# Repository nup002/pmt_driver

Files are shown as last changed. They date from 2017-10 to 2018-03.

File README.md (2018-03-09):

# PMT driver
-------------

The PMT driver is a complete system for operating and pulse height triggering on up to four photomultiplier tubes. 
It will output high-precision (92ps jitter typ.) trigger pulses from each channel as LVDS signals on cat5 ethernet cable.
Low-precision trigger pulses are combined with programmable logic so that channels can be set up in coincidence, veto, or any other 
configuration as required for the specific experimental setup.

Specifications and capabilities:
- Input voltage: 18V-36V, recommended 24V.
- Current consumption: 250mA
- Screw terminals for powering and controlling gain of four PMTs (designed for Hamamatsu H10425 series)
- Four LEMO input channels. Per channel:
  - 5.95mV/1µA amplifier (75.5dB). Operational range: 1MHz - 300MHz.
  - Pulse height discriminator (200ps jitter typ.) with adjustable discriminator level and pulse length output.
  - Discriminated pulse output as LVDS over RJ45 connector for standard cat5 ethernet cables. Pulses from each of the four channels are time-matched to +-5ps.
- TTL-level version of the discriminated pulses pass through optional delay lines.
- Discriminated pulses are combined with programmable logic, so that nearly any required experimental configuration can be implemented. 
- Final pulse is output over LVDS and TTL, with adjustable length.

## Programmable logic
There are four input channels on the PMT driver, designated CH0 to Ch3. CH0 and CH1 are designed as Pair A. CH2 and CH3 are designated as Pair B. 
The TTL pulses that are generated by each discriminator are combined in a block of programmable logic, where the configuration is set by DIP-switches. There are 
three blocks of DIP-switches. The signals of Pair A are combined in block 1. The signals of Pair B are combined in block 2. 
These two signals are then combined to one in block 3. This is the final output. 

The DIP switches works as lookup tables, and their configuration determine what the output of the block will be based on the logic state of the two input channels. 
Each block can therefore be set up to be any logic gate, such as AND, OR, NOR, XOR, NAND, etc, and also other non-standard logic gates.

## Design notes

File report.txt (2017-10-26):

Info: Reading netlist file "C:\Users\pixel\Documents\Kicad projects\pmt_driver\Netlist.net".

Info: Using references to match components and footprints.

Error: No footprint defined for component 'J2'.

Error: No footprint defined for component 'D1'.

Error: No footprint defined for component 'R25'.

Error: No footprint defined for component 'J6'.

Error: No footprint defined for component 'U9'.

Error: No footprint defined for component 'C62'.

Error: No footprint defined for component 'R27'.

Info: Checking netlist component footprint "C1:/59A05019/59E02E3B:Capacitors_THT:CP_Radial_D10.0mm_P5.00mm".

Adding new component "C1:/59A05019/59E02E3B" footprint "Capacitors_THT:CP_Radial_D10.0mm_P5.00mm".

Info: Checking netlist component footprint "C2:/59A05019/59DFEB5B:Capacitors_THT:CP_Radial_D10.0mm_P5.00mm".

Adding new component "C2:/59A05019/59DFEB5B" footprint "Capacitors_THT:CP_Radial_D10.0mm_P5.00mm".

Info: Checking netlist component footprint "C3:/59A05019/59E0031B:Capacitors_SMD:C_1206_HandSoldering".

Adding new component "C3:/59A05019/59E0031B" footprint "Capacitors_SMD:C_1206_HandSoldering".

Info: Checking netlist component footprint "C4:/59A05019/59E03022:Capacitors_THT:CP_Radial_D8.0mm_P3.50mm".

Adding new component "C4:/59A05019/59E03022" footprint "Capacitors_THT:CP_Radial_D8.0mm_P3.50mm".

Info: Checking netlist component footprint "C5:/59A05019/59DFE2C9:Capacitors_SMD:C_1206_HandSoldering".

Adding new component "C5:/59A05019/59DFE2C9" footprint "Capacitors_SMD:C_1206_HandSoldering".

Info: Checking netlist component footprint "C6:/59A05019/59E04BC9:Capacitors_THT:CP_Radial_D8.0mm_P5.00mm".

Adding new component "C6:/59A05019/59E04BC9" footprint "Capacitors_THT:CP_Radial_D8.0mm_P5.00mm".

Info: Checking netlist component footprint "C7:/59A05019/59E06937:Capacitors_THT:CP_Radial_D8.0mm_P5.00mm".

Adding new component "C7:/59A05019/59E06937" footprint "Capacitors_THT:CP_Radial_D8.0mm_P5.00mm".

Info: Checking netlist component footprint "C8:/59A05019/59E05166:Capacitors_THT:CP_Radial_D8.0mm_P5.00mm".

Adding new component "C8:/59A05019/59E05166" footprint "Capacitors_THT:CP_Radial_D8.0mm_P5.00mm".

Info: Checking netlist component footprint "C9:/59A05019/59E06947:Capacitors_THT:CP_Radial_D8.0mm_P5.00mm".

Adding new component "C9:/59A05019/59E06947" footprint "Capacitors_THT:CP_Radial_D8.0mm_P5.00mm".

Info: Checking netlist component footprint "C10:/59A05019/59E04F1C:Capacitors_SMD:C_1206_HandSoldering".

Adding new component "C10:/59A05019/59E04F1C" footprint "Capacitors_SMD:C_1206_HandSoldering".

Info: Checking netlist component footprint "C11:/59A05019/59E0693F:Capacitors_SMD:C_1206_HandSoldering".

Adding new component "C11:/59A05019/59E0693F" footprint "Capacitors_SMD:C_1206_HandSoldering".

Info: Checking netlist component footprint "C12:/59A05019/59E051E6:Capacitors_SMD:C_1206_HandSoldering".

Adding new component "C12:/59A05019/59E051E6" footprint "Capacitors_SMD:C_1206_HandSoldering".

Info: Checking netlist component footprint "C13:/59A05019/59E0694F:Capacitors_SMD:C_1206_HandSoldering".

Adding new component "C13:/59A05019/59E0694F" footprint "Capacitors_SMD:C_1206_HandSoldering".

Info: Checking netlist component footprint "C14:/59A05019/59DFDE0B:Resistors_SMD:R_1206_HandSoldering".

Adding new component "C14:/59A05019/59DFDE0B" footprint "Resistors_SMD:R_1206_HandSoldering".

Info: Checking netlist component footprint "C15:/59A05019/59A07473:Capacitors_SMD:C_0805_HandSoldering".

Adding new component "C15:/59A05019/59A07473" footprint "Capacitors_SMD:C_0805_HandSoldering".

Info: Checking netlist component footprint "C16:/59A05019/59E06927:Capacitors_SMD:C_0805_HandSoldering".

Adding new component "C16:/59A05019/59E06927" footprint "Capacitors_SMD:C_0805_HandSoldering".

Info: Checking netlist component footprint "C17:/59A05019/59E0525E:Capacitors_SMD:C_0805_HandSoldering".

Adding new component "C17:/59A05019/59E0525E" footprint "Capacitors_SMD:C_0805_HandSoldering".

Info: Checking netlist component footprint "C18:/59A05019/59E06957:Capacitors_SMD:C_0805_HandSoldering".

Adding new component "C18:/59A05019/59E06957" footprint "Capacitors_SMD:C_0805_HandSoldering".

Info: Checking netlist component footprint "C19:/59A05019/59E01262:Capacitors_THT:C_Radial_D5_L11_P2".

Adding new component "C19:/59A05019/59E01262" footprint "Capacitors_THT:C_Radial_D5_L11_P2".

Info: Checking netlist component footprint "C20:/59A05019/59E01A68:Capacitors_THT:CP_Radial_D8.0mm_P3.50mm".

Adding new component "C20:/59A05019/59E01A68" footprint "Capacitors_THT:CP_Radial_D8.0mm_P3.50mm".

Info: Checking netlist component footprint "C21:/59A0A1E6/59DC8F61:Capacitors_SMD:C_0805_HandSoldering".

Adding new component "C21:/59A0A1E6/59DC8F61" footprint "Capacitors_SMD:C_0805_HandSoldering".

Info: Checking netlist component footprint "C22:/59A0A1E6/59DD6348:Capacitors_SMD:C_0805_HandSoldering".

Adding new component "C22:/59A0A1E6/59DD6348" footprint "Capacitors_SMD:C_0805_HandSoldering".

Info: Checking netlist component footprint "C23:/59A0A1E6/59DBDC4C:Capacitors_SMD:C_0402".

Adding new component "C23:/59A0A1E6/59DBDC4C" footprint "Capacitors_SMD:C_0402".

Info: Checking netlist component footprint "C24:/59A0A1E6/59DBE8B8:Capacitors_SMD:C_0402".

Adding new component "C24:/59A0A1E6/59DBE8B8" footprint "Capacitors_SMD:C_0402".

Info: Checking netlist component footprint "C25:/59A0A1E6/59D8314A:Capacitors_SMD:C_0306".

Adding new component "C25:/59A0A1E6/59D8314A" footprint "Capacitors_SMD:C_0306".

Info: Checking netlist component footprint "C26:/59A0A1E6/59DBE89D:Capacitors_SMD:C_0306".

Adding new component "C26:/59A0A1E6/59DBE89D" footprint "Capacitors_SMD:C_0306".

Info: Checking netlist component footprint "C27:/59A0A1E6/59D8318E:Capacitors_SMD:C_0306".

Adding new component "C27:/59A0A1E6/59D8318E" footprint "Capacitors_SMD:C_0306".

Info: Checking netlist component footprint "C28:/59A0A1E6/59DBE8A4:Capacitors_SMD:C_0306".

Adding new component "C28:/59A0A1E6/59DBE8A4" footprint "Capacitors_SMD:C_0306".

Info: Checking netlist component footprint "C29:/59A0A1E6/59DBFA84:Capacitors_SMD:C_0603_HandSoldering".

Adding new component "C29:/59A0A1E6/59DBFA84" footprint "Capacitors_SMD:C_0603_HandSoldering".

Info: Checking netlist component footprint "C30:/59A0A1E6/59DC046C:Capacitors_SMD:C_0402".

Adding new component "C30:/59A0A1E6/59DC046C" footprint "Capacitors_SMD:C_0402".

Info: Checking netlist component footprint "C31:/59A0A1E6/59DC048D:Capacitors_SMD:C_0402".

Adding new component "C31:/59A0A1E6/59DC048D" footprint "Capacitors_SMD:C_0402".

Info: Checking netlist component footprint "C32:/59A0A1E6/59DC0454:Capacitors_SMD:C_0306".

Adding new component "C32:/59A0A1E6/59DC0454" footprint "Capacitors_SMD:C_0306".

Info: Checking netlist component footprint "C33:/59A0A1E6/59DC0475:Capacitors_SMD:C_0306".

Adding new component "C33:/59A0A1E6/59DC0475" footprint "Capacitors_SMD:C_0306".

Info: Checking netlist component footprint "C34:/59A0A1E6/59DD625D:Capacitors_SMD:C_0306".

Adding new component "C34:/59A0A1E6/59DD625D" footprint "Capacitors_SMD:C_0306".

Info: Checking netlist component footprint "C35:/59A0A1E6/59DC047C:Capacitors_SMD:C_0306".

Adding new component "C35:/59A0A1E6/59DC047C" footprint "Capacitors_SMD:C_0306".

Info: Checking netlist component footprint "C36:/59A0A1E6/59DC045B:Capacitors_SMD:C_0306".

Adding new component "C36:/59A0A1E6/59DC045B" footprint "Capacitors_SMD:C_0306".

Info: Checking netlist component footprint "C37:/59A0A1E6/59DBF0A4:Capacitors_SMD:C_0603_HandSoldering".

Adding new component "C37:/59A0A1E6/59DBF0A4" footprint "Capacitors_SMD:C_0603_HandSoldering".

Info: Checking netlist component footprint "C38:/59A0A1E6/59DC2B62:Capacitors_SMD:C_0402".

Adding new component "C38:/59A0A1E6/59DC2B62" footprint "Capacitors_SMD:C_0402".

Info: Checking netlist component footprint "C39:/59A0A1E6/59DC2B7E:Capacitors_SMD:C_0402".

Adding new component "C39:/59A0A1E6/59DC2B7E" footprint "Capacitors_SMD:C_0402".

Info: Checking netlist component footprint "C40:/59A0A1E6/59DC2B4D:Capacitors_SMD:C_0306".

Adding new component "C40:/59A0A1E6/59DC2B4D" footprint "Capacitors_SMD:C_0306".

Info: Checking netlist component footprint "C41:/59A0A1E6/59DC2B69:Capacitors_SMD:C_0306".

Adding new component "C41:/59A0A1E6/59DC2B69" footprint "Capacitors_SMD:C_0306".

Info: Checking netlist component footprint "C42:/59A0A1E6/59DC330D:Capacitors_SMD:C_0603_HandSoldering".

Adding new component "C42:/59A0A1E6/59DC330D" footprint "Capacitors_SMD:C_0603_HandSoldering".

Info: Checking netlist component footprint "C43:/59A0A1E6/59DC2B54:Capacitors_SMD:C_0306".

Adding new component "C43:/59A0A1E6/59DC2B54" footprint "Capacitors_SMD:C_0306".

Info: Checking netlist component footprint "C44:/59A0A1E6/59DC2B70:Capacitors_SMD:C_0306".

Adding new component "C44:/59A0A1E6/59DC2B70" footprint "Capacitors_SMD:C_0306".

Info: Checking netlist component footprint "C45:/59A0A1E6/59DC3DE1:Resistors_SMD:R_0603_HandSoldering".

Adding new component "C45:/59A0A1E6/59DC3DE1" footprint "Resistors_SMD:R_0603_HandSoldering".

Info: Checking netlist component footprint "C46:/59A0A1E6/59DC6927:Capacitors_SMD:C_0402".

Adding new component "C46:/59A0A1E6/59DC6927" footprint "Capacitors_SMD:C_0402".

Info: Checking netlist component footprint "C47:/59A0A1E6/59DC6943:Capacitors_SMD:C_0402".

Adding new component "C47:/59A0A1E6/59DC6943" footprint "Capacitors_SMD:C_0402".

Info: Checking netlist component footprint "C48:/59A0A1E6/59DD4C94:Capacitors_SMD:C_0603_HandSoldering".

Adding new component "C48:/59A0A1E6/59DD4C94" footprint "Capacitors_SMD:C_0603_HandSoldering".

Info: Checking netlist component footprint "C49:/59A0A1E6/59DC6912:Capacitors_SMD:C_0306".

Adding new component "C49:/59A0A1E6/59DC6912" footprint "Capacitors_SMD:C_0306".

Info: Checking netlist component footprint "C50:/59A0A1E6/59DC692E:Capacitors_SMD:C_0306".

Adding new component "C50:/59A0A1E6/59DC692E" footprint "Capacitors_SMD:C_0306".

Info: Checking netlist component footprint "C51:/59A0A1E6/59DC6919:Capacitors_SMD:C_0306".

Adding new component "C51:/59A0A1E6/59DC6919" footprint "Capacitors_SMD:C_0306".

Info: Checking netlist component footprint "C52:/59A0A1E6/59DC6935:Capacitors_SMD:C_0306".

Adding new component "C52:/59A0A1E6/59DC6935" footprint "Capacitors_SMD:C_0306".

Info: Checking netlist component footprint "C53:/59A0A213/59DF055C:Resistors_SMD:R_0805_HandSoldering".

Adding new component "C53:/59A0A213/59DF055C" footprint "Resistors_SMD:R_0805_HandSoldering".

Info: Checking netlist component footprint "C54:/59A0A213/59DDFB03:Capacitors_SMD:C_0603_HandSoldering".

Adding new component "C54:/59A0A213/59DDFB03" footprint "Capacitors_SMD:C_0603_HandSoldering".

Info: Checking netlist component footprint "C55:/59A0A213/59DEB078:Resistors_SMD:R_0612".

Adding new component "C55:/59A0A213/59DEB078" footprint "Resistors_SMD:R_0612".

Info: Checking netlist component footprint "C56:/59A0A213/59DEB5CD:Resistors_SMD:R_0612".

Adding new component "C56:/59A0A213/59DEB5CD" footprint "Resistors_SMD:R_0612".

Info: Checking netlist component footprint "C57:/59A0A213/59DF05E1:Resistors_SMD:R_0805_HandSoldering".

Adding new component "C57:/59A0A213/59DF05E1" footprint "Resistors_SMD:R_0805_HandSoldering".

Info: Checking netlist component footprint "C58:/59A0A213/59DEB6B2:Resistors_SMD:R_0612".

Adding new component "C58:/59A0A213/59DEB6B2" footprint "Resistors_SMD:R_0612".

Info: Checking netlist component footprint "C59:/59A0A213/59DEC058:Resistors_SMD:R_0612".

Adding new component "C59:/59A0A213/59DEC058" footprint "Resistors_SMD:R_0612".

Info: Checking netlist component footprint "C60:/59A0A213/59DEB74F:Resistors_SMD:R_0612".

Adding new component "C60:/59A0A213/59DEB74F" footprint "Resistors_SMD:R_0612".

Info: Checking netlist component footprint "C61:/59A0A213/59DEFD9E:Capacitors_SMD:C_0402_NoSilk".

Adding new component "C61:/59A0A213/59DEFD9E" footprint "Capacitors_SMD:C_0402_NoSilk".

Info: Checking netlist component footprint "C62:/59A0A213/59DE27D9:".

Error: Cannot add new component "C62:/59A0A213/59DE27D9" due to missing footprint "".

Info: Checking netlist component footprint "C63:/59A0A213/59DEC751:Resistors_SMD:R_0612".

Adding new component "C63:/59A0A213/59DEC751" footprint "Resistors_SMD:R_0612".

Info: Checking netlist component footprint "C64:/59A0A213/59DEC7C9:Resistors_SMD:R_0612".

Adding new component "C64:/59A0A213/59DEC7C9" footprint "Resistors_SMD:R_0612".

Info: Checking netlist component footprint "C65:/59A0A213/59DED289:Capacitors_SMD:C_0402_NoSilk".

Adding new component "C65:/59A0A213/59DED289" footprint "Capacitors_SMD:C_0402_NoSilk".

Info: Checking netlist component footprint "C66:/59E272DD/59E293CD:Capacitors_SMD:C_0805_HandSoldering".

Adding new component "C66:/59E272DD/59E293CD" footprint "Capacitors_SMD:C_0805_HandSoldering".

Info: Checking netlist component footprint "C67:/59E272DD/59E2A45B:Capacitors_SMD:C_0805_HandSoldering".

Adding new component "C67:/59E272DD/59E2A45B" footprint "Capacitors_SMD:C_0805_HandSoldering".

Info: Checking netlist component footprint "C68:/59E272DD/59E2A7D9:Capacitors_SMD:C_0805_HandSoldering".

Adding new component "C68:/59E272DD/59E2A7D9" footprint "Capacitors_SMD:C_0805_HandSoldering".

Info: Checking netlist component footprint "C69:/59E272DD/59E2A7FF:Capacitors_SMD:C_0805_HandSoldering".

Adding new component "C69:/59E272DD/59E2A7FF" footprint "Capacitors_SMD:C_0805_HandSoldering".

Info: Checking netlist component footprint "C70:/59E35431/59E35B6A:Capacitors_SMD:C_0603_HandSoldering".

Adding new component "C70:/59E35431/59E35B6A" footprint "Capacitors_SMD:C_0603_HandSoldering".

Info: Checking netlist component footprint "C71:/59E35431/59E3A291:Capacitors_SMD:C_0603_HandSoldering".

Adding new component "C71:/59E35431/59E3A291" footprint "Capacitors_SMD:C_0603_HandSoldering".

Info: Checking netlist component footprint "C72:/59E35431/59E3E4E3:Capacitors_SMD:C_0603_HandSoldering".

Adding new component "C72:/59E35431/59E3E4E3" footprint "Capacitors_SMD:C_0603_HandSoldering".

Info: Checking netlist component footprint "C73:/59E35431/59E3E557:Capacitors_SMD:C_0603_HandSoldering".

Adding new component "C73:/59E35431/59E3E557" footprint "Capacitors_SMD:C_0603_HandSoldering".

Info: Checking netlist component footprint "C74:/59E35431/59E3E5BA:Capacitors_SMD:C_0603_HandSoldering".

Adding new component "C74:/59E35431/59E3E5BA" footprint "Capacitors_SMD:C_0603_HandSoldering".

Info: Checking netlist component footprint "C75:/59E35431/59E3A495:Capacitors_SMD:C_0603_HandSoldering".

Adding new component "C75:/59E35431/59E3A495" footprint "Capacitors_SMD:C_0603_HandSoldering".

Info: Checking netlist component footprint "D1:/59A05019/59DFEEB0:".

Error: Cannot add new component "D1:/59A05019/59DFEEB0" due to missing footprint "".

Info: Checking netlist component footprint "D2:/59A05019/59DFC2FB:Diodes_THT:D_DO-41_SOD81_P10.16mm_Horizontal".

Adding new component "D2:/59A05019/59DFC2FB" footprint "Diodes_THT:D_DO-41_SOD81_P10.16mm_Horizontal".

Info: Checking netlist component footprint "D3:/59A0A213/59DF393A:Diodes_SMD:SOD-523".

Adding new component "D3:/59A0A213/59DF393A" footprint "Diodes_SMD:SOD-523".

Info: Checking netlist component footprint "D4:/59A0A213/59DF41EE:Diodes_SMD:SOD-523".

Adding new component "D4:/59A0A213/59DF41EE" footprint "Diodes_SMD:SOD-523".

Info: Checking netlist component footprint "D5:/59A0A213/59DF2D95:Diodes_SMD:D_MiniMELF_Handsoldering".

Adding new component "D5:/59A0A213/59DF2D95" footprint "Diodes_SMD:D_MiniMELF_Handsoldering".

Info: Checking netlist component footprint "D6:/59A0A213/59DE301E:Diodes_SMD:D_MiniMELF_Handsoldering".

Adding new component "D6:/59A0A213/59DE301E" footprint "Diodes_SMD:D_MiniMELF_Handsoldering".

Info: Checking netlist component footprint "F1:/59A05019/59E08890:Fuse_Holders_and_Fuses:Littelfuse_05200101Z_holder".

Adding new component "F1:/59A05019/59E08890" footprint "Fuse_Holders_and_Fuses:Littelfuse_05200101Z_holder".

Info: Checking netlist component footprint "J1:/59DDBB95:Connectors:LEMO_angled".

Adding new component "J1:/59DDBB95" footprint "Connectors:LEMO_angled".

Info: Checking netlist component footprint "J2:/59E2DD03:".

Error: Cannot add new component "J2:/59E2DD03" due to missing footprint "".

Info: Checking netlist component footprint "J3:/59E1F4E1:Connectors:LEMO_straight".

Adding new component "J3:/59E1F4E1" footprint "Connectors:LEMO_straight".

Info: Checking netlist component footprint "J4:/59E230FE/59E237F4:Connectors:LEMO_straight".

Adding new component "J4:/59E230FE/59E237F4" footprint "Connectors:LEMO_straight".

Info: Checking netlist component footprint "J5:/59E230FE/59E23908:Connectors:LEMO_straight".

Adding new component "J5:/59E230FE/59E23908" footprint "Connectors:LEMO_straight".

Info: Checking netlist component footprint "J6:/59E230FE/59E237AA:".

Error: Cannot add new component "J6:/59E230FE/59E237AA" due to missing footprint "".

Info: Checking netlist component footprint "J7:/59E272DD/59E29675:Connectors_Terminal_Blocks:TerminalBlock_Pheonix_MPT-2.54mm_4pol".

Adding new component "J7:/59E272DD/59E29675" footprint "Connectors_Terminal_Blocks:TerminalBlock_Pheonix_MPT-2.54mm_4pol".

Info: Checking netlist component footprint "J8:/59E272DD/59E2A465:Connectors_Terminal_Blocks:TerminalBlock_Pheonix_MPT-2.54mm_4pol".

Adding new component "J8:/59E272DD/59E2A465" footprint "Connectors_Terminal_Blocks:TerminalBlock_Pheonix_MPT-2.54mm_4pol".

Info: Checking netlist component footprint "J9:/59E272DD/59E2A7E3:Connectors_Terminal_Blocks:TerminalBlock_Pheonix_MPT-2.54mm_4pol".

Adding new component "J9:/59E272DD/59E2A7E3" footprint "Connectors_Terminal_Blocks:TerminalBlock_Pheonix_MPT-2.54mm_4pol".

Info: Checking netlist component footprint "J10:/59E272DD/59E2A809:Connectors_Terminal_Blocks:TerminalBlock_Pheonix_MPT-2.54mm_4pol".

Adding new component "J10:/59E272DD/59E2A809" footprint "Connectors_Terminal_Blocks:TerminalBlock_Pheonix_MPT-2.54mm_4pol".

Info: Checking netlist component footprint "JP1:/59E230FE/59E23962:Pin_Headers:Pin_Header_Straight_1x02_Pitch2.54mm".

Adding new component "JP1:/59E230FE/59E23962" footprint "Pin_Headers:Pin_Header_Straight_1x02_Pitch2.54mm".

Info: Checking netlist component footprint "L1:/59A05019/59DFE9CD:Inductors_THT:L_Toroid_Vertical_L22.4mm_W10.2mm_P7.90mm_Vishay_TJ4".

Adding new component "L1:/59A05019/59DFE9CD" footprint "Inductors_THT:L_Toroid_Vertical_L22.4mm_W10.2mm_P7.90mm_Vishay_TJ4".

Info: Checking netlist component footprint "L2:/59A05019/59E03142:Inductors_THT:L_Radial_D10.0mm_P5.00mm_Fastron_07M".

Adding new component "L2:/59A05019/59E03142" footprint "Inductors_THT:L_Radial_D10.0mm_P5.00mm_Fastron_07M".

Info: Checking netlist component footprint "L3:/59A05019/59DFE748:Inductors_THT:L_Radial_D6.0mm_P4.00mm".

Adding new component "L3:/59A05019/59DFE748" footprint "Inductors_THT:L_Radial_D6.0mm_P4.00mm".

Info: Checking netlist component footprint "L4:/59A05019/59A07609:Inductors_THT:L_Radial_D12.0mm_P6.5mm".

Adding new component "L4:/59A05019/59A07609" footprint "Inductors_THT:L_Radial_D12.0mm_P6.5mm".

Info: Checking netlist component footprint "L5:/59A05019/59E0692F:Inductors_THT:L_Radial_D12.0mm_P6.5mm".

Adding new component "L5:/59A05019/59E0692F" footprint "Inductors_THT:L_Radial_D12.0mm_P6.5mm".

Info: Checking netlist component footprint "L6:/59A0A1E6/59DBD9B5:Inductors_SMD:L_1210".

Adding new component "L6:/59A0A1E6/59DBD9B5" footprint "Inductors_SMD:L_1210".

Info: Checking netlist component footprint "L7:/59A0A1E6/59DBE8B1:Inductors_SMD:L_1210".

Adding new component "L7:/59A0A1E6/59DBE8B1" footprint "Inductors_SMD:L_1210".

Info: Checking netlist component footprint "L8:/59A0A1E6/59DC0465:Inductors_SMD:L_1210".

Adding new component "L8:/59A0A1E6/59DC0465" footprint "Inductors_SMD:L_1210".

Info: Checking netlist component footprint "L9:/59A0A1E6/59DC0486:Inductors_SMD:L_1210".

Adding new component "L9:/59A0A1E6/59DC0486" footprint "Inductors_SMD:L_1210".

Info: Checking netlist component footprint "L10:/59A0A1E6/59DC2B5B:Inductors_SMD:L_1210".

Adding new component "L10:/59A0A1E6/59DC2B5B" footprint "Inductors_SMD:L_1210".

Info: Checking netlist component footprint "L11:/59A0A1E6/59DC2B77:Inductors_SMD:L_1210".

Adding new component "L11:/59A0A1E6/59DC2B77" footprint "Inductors_SMD:L_1210".

Info: Checking netlist component footprint "L12:/59A0A1E6/59DC6920:Inductors_SMD:L_1210".

Adding new component "L12:/59A0A1E6/59DC6920" footprint "Inductors_SMD:L_1210".

Info: Checking netlist component footprint "L13:/59A0A1E6/59DC693C:Inductors_SMD:L_1210".

Adding new component "L13:/59A0A1E6/59DC693C" footprint "Inductors_SMD:L_1210".

Info: Checking netlist component footprint "P1:/59A05019/59DFB0AF:Modules:JCH1024D05".

Adding new component "P1:/59A05019/59DFB0AF" footprint "Modules:JCH1024D05".

Info: Checking netlist component footprint "P2:/59A05019/59DFBA0F:Modules:PQMC3-S".

Adding new component "P2:/59A05019/59DFBA0F" footprint "Modules:PQMC3-S".

Info: Checking netlist component footprint "R1:/59E20290:Resistors_SMD:R_0805_HandSoldering".

Adding new component "R1:/59E20290" footprint "Resistors_SMD:R_0805_HandSoldering".

Info: Checking netlist component footprint "R2:/59A05019/59E09FFE:Resistors_SMD:R_0603_HandSoldering".

Adding new component "R2:/59A05019/59E09FFE" footprint "Resistors_SMD:R_0603_HandSoldering".

Info: Checking netlist component footprint "R3:/59A05019/59E0A169:Resistors_SMD:R_2010_HandSoldering".

Adding new component "R3:/59A05019/59E0A169" footprint "Resistors_SMD:R_2010_HandSoldering".

Info: Checking netlist component footprint "R4:/59A05019/59DFC20B:Resistors_SMD:R_0805_HandSoldering".

Adding new component "R4:/59A05019/59DFC20B" footprint "Resistors_SMD:R_0805_HandSoldering".

Info: Checking netlist component footprint "R5:/59A05019/59E05721:Resistors_SMD:R_1206_HandSoldering".

Adding new component "R5:/59A05019/59E05721" footprint "Resistors_SMD:R_1206_HandSoldering".

Info: Checking netlist component footprint "R6:/59A05019/59E06972:Resistors_SMD:R_1206_HandSoldering".

Adding new component "R6:/59A05019/59E06972" footprint "Resistors_SMD:R_1206_HandSoldering".

Info: Checking netlist component footprint "R7:/59A05019/59E1658C:Resistors_SMD:R_0805_HandSoldering".

Adding new component "R7:/59A05019/59E1658C" footprint "Resistors_SMD:R_0805_HandSoldering".

Info: Checking netlist component footprint "R8:/59A05019/59E1661F:Resistors_SMD:R_0805_HandSoldering".

Adding new component "R8:/59A05019/59E1661F" footprint "Resistors_SMD:R_0805_HandSoldering".

Info: Checking netlist component footprint "R9:/59A05019/59E16438:Resistors_SMD:R_0805_HandSoldering".

Adding new component "R9:/59A05019/59E16438" footprint "Resistors_SMD:R_0805_HandSoldering".

Info: Checking netlist component footprint "R10:/59A05019/59E164F9:Resistors_SMD:R_0805_HandSoldering".

Adding new component "R10:/59A05019/59E164F9" footprint "Resistors_SMD:R_0805_HandSoldering".

Info: Checking netlist component footprint "R11:/59A0A1E6/59D7DCA4:Resistors_SMD:R_0805_HandSoldering".

Adding new component "R11:/59A0A1E6/59D7DCA4" footprint "Resistors_SMD:R_0805_HandSoldering".

Info: Checking netlist component footprint "R12:/59A0A1E6/59DBF45E:Resistors_SMD:R_0603_HandSoldering".

Adding new component "R12:/59A0A1E6/59DBF45E" footprint "Resistors_SMD:R_0603_HandSoldering".

Info: Checking netlist component footprint "R13:/59A0A1E6/59DCD1D7:Resistors_SMD:R_0603_HandSoldering".

Adding new component "R13:/59A0A1E6/59DCD1D7" footprint "Resistors_SMD:R_0603_HandSoldering".

Info: Checking netlist component footprint "R14:/59A0A1E6/59DBF9C3:Resistors_SMD:R_0603_HandSoldering".

Adding new component "R14:/59A0A1E6/59DBF9C3" footprint "Resistors_SMD:R_0603_HandSoldering".

Info: Checking netlist component footprint "R15:/59A0A1E6/59DBF09E:Capacitors_SMD:C_0805_HandSoldering".

Adding new component "R15:/59A0A1E6/59DBF09E" footprint "Capacitors_SMD:C_0805_HandSoldering".

Info: Checking netlist component footprint "R16:/59A0A1E6/59DD36C3:Resistors_SMD:R_0603_HandSoldering".

Adding new component "R16:/59A0A1E6/59DD36C3" footprint "Resistors_SMD:R_0603_HandSoldering".

Info: Checking netlist component footprint "R17:/59A0A1E6/59DD346D:Resistors_SMD:R_0603_HandSoldering".

Adding new component "R17:/59A0A1E6/59DD346D" footprint "Resistors_SMD:R_0603_HandSoldering".

Info: Checking netlist component footprint "R18:/59A0A1E6/59DC3301:Resistors_SMD:R_0402".

Adding new component "R18:/59A0A1E6/59DC3301" footprint "Resistors_SMD:R_0402".

Info: Checking netlist component footprint "R19:/59A0A213/59E0FCD1:Resistors_SMD:R_0805_HandSoldering".

Adding new component "R19:/59A0A213/59E0FCD1" footprint "Resistors_SMD:R_0805_HandSoldering".

Info: Checking netlist component footprint "R20:/59A0A213/59DF4700:Resistors_SMD:R_0603_HandSoldering".

Adding new component "R20:/59A0A213/59DF4700" footprint "Resistors_SMD:R_0603_HandSoldering".

Info: Checking netlist component footprint "R21:/59A0A213/59DDFE5E:Resistors_SMD:R_0805_HandSoldering".

Adding new component "R21:/59A0A213/59DDFE5E" footprint "Resistors_SMD:R_0805_HandSoldering".

Info: Checking netlist component footprint "R22:/59A0A213/59DDFD70:Resistors_SMD:R_0805_HandSoldering".

Adding new component "R22:/59A0A213/59DDFD70" footprint "Resistors_SMD:R_0805_HandSoldering".

Info: Checking netlist component footprint "R23:/59A0A213/59DE24D1:Resistors_SMD:R_0805_HandSoldering".

Adding new component "R23:/59A0A213/59DE24D1" footprint "Resistors_SMD:R_0805_HandSoldering".

Info: Checking netlist component footprint "R24:/59A0A213/59DE19F7:Resistors_SMD:R_0603_HandSoldering".

Adding new component "R24:/59A0A213/59DE19F7" footprint "Resistors_SMD:R_0603_HandSoldering".

Info: Checking netlist component footprint "R25:/59A0A213/59DE1BBC:".

Error: Cannot add new component "R25:/59A0A213/59DE1BBC" due to missing footprint "".

Info: Checking netlist component footprint "R26:/59A0A213/59DE1AAB:Resistors_SMD:R_0603_HandSoldering".

Adding new component "R26:/59A0A213/59DE1AAB" footprint "Resistors_SMD:R_0603_HandSoldering".

Info: Checking netlist component footprint "R27:/59A0A213/59DE1C61:".

Error: Cannot add new component "R27:/59A0A213/59DE1C61" due to missing footprint "".

Info: Checking netlist component footprint "R28:/59E272DD/59E29961:Resistors_SMD:R_0805_HandSoldering".

Adding new component "R28:/59E272DD/59E29961" footprint "Resistors_SMD:R_0805_HandSoldering".

Info: Checking netlist component footprint "R29:/59E272DD/59E2A46B:Resistors_SMD:R_0805_HandSoldering".

Adding new component "R29:/59E272DD/59E2A46B" footprint "Resistors_SMD:R_0805_HandSoldering".

Info: Checking netlist component footprint "R30:/59E272DD/59E2A7E9:Resistors_SMD:R_0805_HandSoldering".

Adding new component "R30:/59E272DD/59E2A7E9" footprint "Resistors_SMD:R_0805_HandSoldering".

Info: Checking netlist component footprint "R31:/59E272DD/59E2A80F:Resistors_SMD:R_0805_HandSoldering".

Adding new component "R31:/59E272DD/59E2A80F" footprint "Resistors_SMD:R_0805_HandSoldering".

Info: Checking netlist component footprint "R32:/59E35431/59E358EE:Resistors_SMD:R_0603_HandSoldering".

Adding new component "R32:/59E35431/59E358EE" footprint "Resistors_SMD:R_0603_HandSoldering".

Info: Checking netlist component footprint "R33:/59E35431/59E3A28B:Resistors_SMD:R_0603_HandSoldering".

Adding new component "R33:/59E35431/59E3A28B" footprint "Resistors_SMD:R_0603_HandSoldering".

Info: Checking netlist component footprint "R34:/59E35431/59E36285:Resistors_SMD:R_0603_HandSoldering".

Adding new component "R34:/59E35431/59E36285" footprint "Resistors_SMD:R_0603_HandSoldering".

Info: Checking netlist component footprint "R35:/59E35431/59E3A2AE:Resistors_SMD:R_0603_HandSoldering".

Adding new component "R35:/59E35431/59E3A2AE" footprint "Resistors_SMD:R_0603_HandSoldering".

Info: Checking netlist component footprint "R36:/59E35431/59E362A7:Resistors_SMD:R_0603_HandSoldering".

Adding new component "R36:/59E35431/59E362A7" footprint "Resistors_SMD:R_0603_HandSoldering".

Info: Checking netlist component footprint "R37:/59E35431/59E3A2B6:Resistors_SMD:R_0603_HandSoldering".

Adding new component "R37:/59E35431/59E3A2B6" footprint "Resistors_SMD:R_0603_HandSoldering".

Info: Checking netlist component footprint "R38:/59E35431/59E362CC:Resistors_SMD:R_0603_HandSoldering".

Adding new component "R38:/59E35431/59E362CC" footprint "Resistors_SMD:R_0603_HandSoldering".

Info: Checking netlist component footprint "R39:/59E35431/59E3A2BE:Resistors_SMD:R_0603_HandSoldering".

Adding new component "R39:/59E35431/59E3A2BE" footprint "Resistors_SMD:R_0603_HandSoldering".

Info: Checking netlist component footprint "R40:/59E35431/59E3A48F:Resistors_SMD:R_0603_HandSoldering".

Adding new component "R40:/59E35431/59E3A48F" footprint "Resistors_SMD:R_0603_HandSoldering".

Info: Checking netlist component footprint "R41:/59E35431/59E3A4B2:Resistors_SMD:R_0603_HandSoldering".

Adding new component "R41:/59E35431/59E3A4B2" footprint "Resistors_SMD:R_0603_HandSoldering".

Info: Checking netlist component footprint "R42:/59E35431/59E3A4BA:Resistors_SMD:R_0603_HandSoldering".

Adding new component "R42:/59E35431/59E3A4BA" footprint "Resistors_SMD:R_0603_HandSoldering".

Info: Checking netlist component footprint "R43:/59E35431/59E3A4C2:Resistors_SMD:R_0603_HandSoldering".

Adding new component "R43:/59E35431/59E3A4C2" footprint "Resistors_SMD:R_0603_HandSoldering".

Info: Checking netlist component footprint "RV1:/59A0A213/59DF2A12:Potentiometers:Potentiometer_Trimmer_Bourns_3266W".

Adding new component "RV1:/59A0A213/59DF2A12" footprint "Potentiometers:Potentiometer_Trimmer_Bourns_3266W".

Info: Checking netlist component footprint "RV2:/59A0A213/59DE23B2:Potentiometers:Potentiometer_Trimmer_Bourns_3266W".

Adding new component "RV2:/59A0A213/59DE23B2" footprint "Potentiometers:Potentiometer_Trimmer_Bourns_3266W".

Info: Checking netlist component footprint "RV3:/59E272DD/59E2873F:Potentiometers:Potentiometer_Trimmer_Bourns_3266W".

Adding new component "RV3:/59E272DD/59E2873F" footprint "Potentiometers:Potentiometer_Trimmer_Bourns_3266W".

Info: Checking netlist component footprint "RV4:/59E272DD/59E2A455:Potentiometers:Potentiometer_Trimmer_Bourns_3266W".

Adding new component "RV4:/59E272DD/59E2A455" footprint "Potentiometers:Potentiometer_Trimmer_Bourns_3266W".

Info: Checking netlist component footprint "RV5:/59E272DD/59E2A7D3:Potentiometers:Potentiometer_Trimmer_Bourns_3266W".

Adding new component "RV5:/59E272DD/59E2A7D3" footprint "Potentiometers:Potentiometer_Trimmer_Bourns_3266W".

Info: Checking netlist component footprint "RV6:/59E272DD/59E2A7F9:Potentiometers:Potentiometer_Trimmer_Bourns_3266W".

Adding new component "RV6:/59E272DD/59E2A7F9" footprint "Potentiometers:Potentiometer_Trimmer_Bourns_3266W".

Info: Checking netlist component footprint "U1:/59A05019/59DFD5C2:Modules:MHPS2283".

Adding new component "U1:/59A05019/59DFD5C2" footprint "Modules:MHPS2283".

Info: Checking netlist component footprint "U2:/59A0A1E6/59D805E4:TO_SOT_Packages_SMD:SOT-23-5_HandSoldering".

Adding new component "U2:/59A0A1E6/59D805E4" footprint "TO_SOT_Packages_SMD:SOT-23-5_HandSoldering".

Info: Checking netlist component footprint "U3:/59A0A1E6/59DBF963:TO_SOT_Packages_SMD:SOT-23-6_Handsoldering".

Adding new component "U3:/59A0A1E6/59DBF963" footprint "TO_SOT_Packages_SMD:SOT-23-6_Handsoldering".

Info: Checking netlist component footprint "U4:/59A0A1E6/59DD8C24:TO_SOT_Packages_SMD:SOT-23-5_HandSoldering".

Adding new component "U4:/59A0A1E6/59DD8C24" footprint "TO_SOT_Packages_SMD:SOT-23-5_HandSoldering".

Info: Checking netlist component footprint "U5:/59A0A1E6/59DD8CE0:TO_SOT_Packages_SMD:SOT-23-6_Handsoldering".

Adding new component "U5:/59A0A1E6/59DD8CE0" footprint "TO_SOT_Packages_SMD:SOT-23-6_Handsoldering".

Info: Checking netlist component footprint "U6:/59A0A213/59DDE4A8:Housings_SSOP:MSOP-10_3x3mm_Pitch0.5mm".

Adding new component "U6:/59A0A213/59DDE4A8" footprint "Housings_SSOP:MSOP-10_3x3mm_Pitch0.5mm".

Info: Checking netlist component footprint "U7:/59A0A213/59DDE9A1:TO_SOT_Packages_SMD:SOT-23-5_HandSoldering".

Adding new component "U7:/59A0A213/59DDE9A1" footprint "TO_SOT_Packages_SMD:SOT-23-5_HandSoldering".

Info: Checking netlist component footprint "U8:/59A0A213/59DDE822:TO_SOT_Packages_SMD:SOT-23-5_HandSoldering".

Adding new component "U8:/59A0A213/59DDE822" footprint "TO_SOT_Packages_SMD:SOT-23-5_HandSoldering".

Info: Checking netlist component footprint "U9:/59A0A213/59DE6545:".

Error: Cannot add new component "U9:/59A0A213/59DE6545" due to missing footprint "".

Info: Checking netlist component footprint "U10:/59A0A213/59DDD94C:Housings_SSOP:MSOP-8_3x3mm_Pitch0.65mm".

Adding new component "U10:/59A0A213/59DDD94C" footprint "Housings_SSOP:MSOP-8_3x3mm_Pitch0.65mm".

Info: Checking netlist component footprint "U11:/59A0A213/59DDDC5C:Housings_SOIC:SOIC-8_3.9x4.9mm_Pitch1.27mm".

Adding new component "U11:/59A0A213/59DDDC5C" footprint "Housings_SOIC:SOIC-8_3.9x4.9mm_Pitch1.27mm".

Info: Checking netlist component footprint "U12:/59E35431/59E35868:Buttons_Switches_THT:SW_DIP_x4_W7.62mm_Slide".

Adding new component "U12:/59E35431/59E35868" footprint "Buttons_Switches_THT:SW_DIP_x4_W7.62mm_Slide".

Info: Checking netlist component footprint "U13:/59E35431/59E3A283:Buttons_Switches_THT:SW_DIP_x4_W7.62mm_Slide".

Adding new component "U13:/59E35431/59E3A283" footprint "Buttons_Switches_THT:SW_DIP_x4_W7.62mm_Slide".

Info: Checking netlist component footprint "U14:/59E35431/59E356F9:Housings_SSOP:MSOP-10_3x3mm_Pitch0.5mm".

Adding new component "U14:/59E35431/59E356F9" footprint "Housings_SSOP:MSOP-10_3x3mm_Pitch0.5mm".

Info: Checking netlist component footprint "U15:/59E35431/59E3A27B:Housings_SSOP:MSOP-10_3x3mm_Pitch0.5mm".

Adding new component "U15:/59E35431/59E3A27B" footprint "Housings_SSOP:MSOP-10_3x3mm_Pitch0.5mm".

Info: Checking netlist component footprint "U16:/59E35431/59E3A47F:Housings_SSOP:MSOP-10_3x3mm_Pitch0.5mm".

Adding new component "U16:/59E35431/59E3A47F" footprint "Housings_SSOP:MSOP-10_3x3mm_Pitch0.5mm".

Info: Checking netlist component footprint "U17:/59E35431/59E3A487:Buttons_Switches_THT:SW_DIP_x4_W7.62mm_Slide".

Adding new component "U17:/59E35431/59E3A487" footprint "Buttons_Switches_THT:SW_DIP_x4_W7.62mm_Slide".

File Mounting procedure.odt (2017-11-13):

Step 1

Mount all components in Sch. “Power”.

Test that the correct voltages on voltage rails are being produced. LEDs should light up. Use test points near LEDs for easy measurement.

Step 2

Mount all components in Sch. “Amplifier”. Also mount coaxial connectors J1 and J4, and resistor R1 (located on first page of schematics). Test the amplifier by connecting an oscilloscope with a bandwidth greater than 350MHz to J4 (oscilloscope input must be terminated in >>50ohm), and plug a signal generator with bandwidth greater than 350MHz to J1. The input signal must be a negative square pulse with maximum negative amplitude of 10mV and length of 150ns. Greater values than 30mV can damage the amplifier. The output of the amplifier should look as follows:

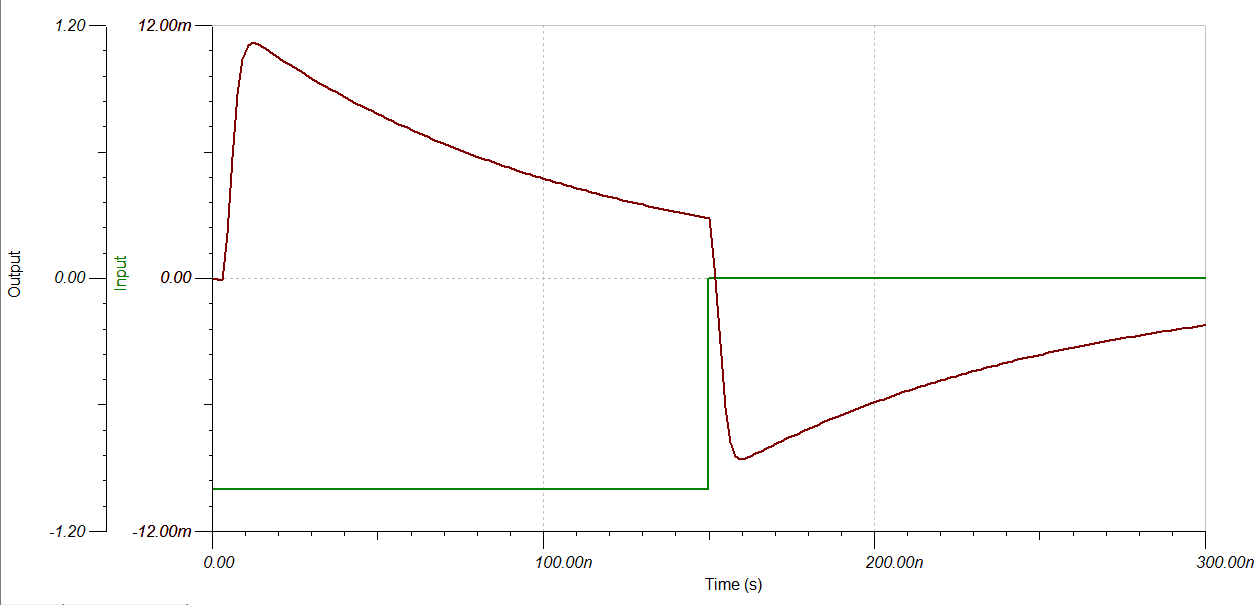
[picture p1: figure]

Measure the noise spectrum of the amplifier output with nothing connected to the input coaxial connector. Contact me (Magne Lauritzen, room 50B 5239, melauritzen@lbl.gov) at this point so I can verify that it is behaving as expected.

Step 3:

On Sch. “Discriminator”, mount components in block labeled “level threshold adjust”. Verify that the discriminator threshold adjuster works by adjusting RV1 and monitoring the output of U7. It should go from 0V to 3V. Mount blocks labelled “protection” and apply the same -10mV input signal to the amplifier while measuring the amplifier output as in step 2. It should look as follows:

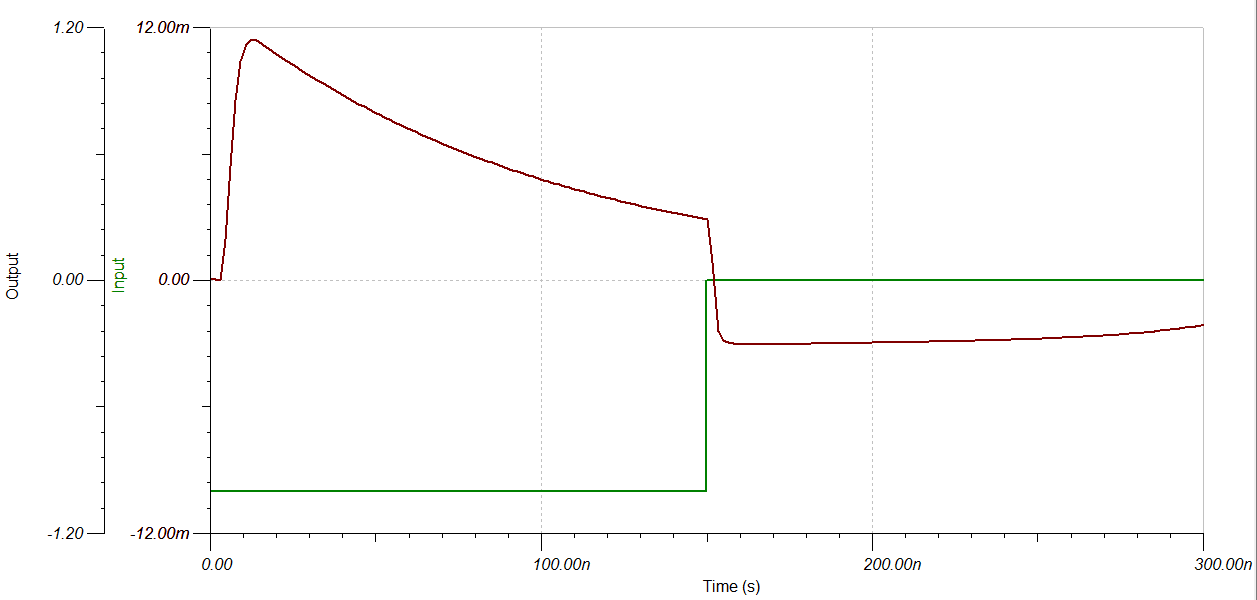
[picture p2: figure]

Mount the blocks labelled“discriminator” and “termination”. Verify that the discriminator works by doing the following:

    1. Adjust the discriminator threshold to around 600mV.
    2. Insert the -10mV square pulse on the amplifier input as you did when testing the amplifier.
    3. Monitor the positive discriminator output (Q, pin 6). It should go from 1.6V to 2.4V (or thereabouts) when the input signal is above 600mV.

Mount the components in the blocks named “Output”. Test the outputs by repeating the previous steps 1-2 while monitoring TTL_OUT and the two LVDS_OUT pins.

Mount the components in the block “Timer”. Test that it works by doing the following:

    1. Apply a short (10-50ns) -10mV square pulse on the amplifier input while monitoring the TTL_OUT pin.
    2. Adjust the potentiometer RV2. The length of the output pulse should vary accordingly.

Step 4:

If everything has gone well until now, mount all the other components on the board.

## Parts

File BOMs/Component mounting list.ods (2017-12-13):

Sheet: Resistors
Ref | Value | MPN | DK | Footprint
R1 | 50 |  |  | Resistors_SMD:R_0805
R2 | 400m | PT2512FK-070R4L | 311-0.4ARCT-ND | Resistors_SMD:R_0603_HandSoldering
R3 | 300m | CSR2010JTR300 | CSR2010JTR300CT-ND | Resistors_SMD:R_2010_HandSoldering
R4 | 2.67k |  |  | Resistors_SMD:R_0805_HandSoldering
R5 | 180m | RL1206FR-070R18L | 311-0.18LWCT-ND | Resistors_SMD:R_1206_HandSoldering
R6 | 180m | RL1206FR-070R18L | 311-0.18LWCT-ND | Resistors_SMD:R_1206_HandSoldering
R7 | 470 |  |  | Resistors_SMD:R_0805_HandSoldering
R8 | 910 |  |  | Resistors_SMD:R_0805_HandSoldering
R9 | 200 |  |  | Resistors_SMD:R_0805_HandSoldering
R10 | 800 |  |  | Resistors_SMD:R_0805_HandSoldering
R11 | 50 |  |  | Resistors_SMD:R_0805
R12 | 39 | RC0603FR-0739RL | 311-39.0HRTR-ND | Resistors_SMD:R_0603
R13 | 39 | RC0603FR-0739RL | 311-39.0HRTR-ND | Resistors_SMD:R_0603
R14 | 470 | RC0603FR-07470RL | 311-470HRCT-ND | Resistors_SMD:R_0603
R15 | 3.3k |  |  | Resistors_SMD:R_0805
R16 | 39 | RC0603FR-0739RL | 311-39.0HRTR-ND | Resistors_SMD:R_0603
R17 | 39 | RC0603FR-0739RL | 311-39.0HRTR-ND | Resistors_SMD:R_0603
R18 | 470 | RC0402FR-07402RL | YAG3152CT-ND | Resistors_SMD:R_0402
R19 | 6.8k |  |  | Resistors_SMD:R_0805
R20 | 50 |  |  | Resistors_SMD:R_0805
R21 | 6.8k |  |  | Resistors_SMD:R_0805
R22 | 1k |  |  | Resistors_SMD:R_0805
R23 | 200 |  |  | Resistors_SMD:R_0805
R24 | 82.5 | RC0603FR-0782R5L | 311-82.5HRCT-ND | Resistors_SMD:R_0603
R25 | 124 | RC0603FR-07124RL | 311-124HRCT-ND | Resistors_SMD:R_0603
R26 | 82.5 | RC0603FR-0782R5L | 311-82.5HRCT-ND | Resistors_SMD:R_0603
R27 | 124 | RC0603FR-07124RL | 311-124HRCT-ND | Resistors_SMD:R_0603
R28 | 10k | RC0603JR-0710KL | 311-10KGRCT-ND | Resistors_SMD:R_0603_HandSoldering
R29 | 10k | RC0603JR-0710KL | 311-10KGRCT-ND | Resistors_SMD:R_0603_HandSoldering
R30 | 10k | RC0603JR-0710KL | 311-10KGRCT-ND | Resistors_SMD:R_0603_HandSoldering
R31 | 10k | RC0603JR-0710KL | 311-10KGRCT-ND | Resistors_SMD:R_0603_HandSoldering
R32 | 10k | RC0603JR-0710KL | 311-10KGRCT-ND | Resistors_SMD:R_0603_HandSoldering
R33 | 10k | RC0603JR-0710KL | 311-10KGRCT-ND | Resistors_SMD:R_0603_HandSoldering
R34 | 10k | RC0603JR-0710KL | 311-10KGRCT-ND | Resistors_SMD:R_0603_HandSoldering
R35 | 10k | RC0603JR-0710KL | 311-10KGRCT-ND | Resistors_SMD:R_0603_HandSoldering
R36 | 10k | RC0603JR-0710KL | 311-10KGRCT-ND | Resistors_SMD:R_0603_HandSoldering
R37 | 10k | RC0603JR-0710KL | 311-10KGRCT-ND | Resistors_SMD:R_0603_HandSoldering
R38 | 10k | RC0603JR-0710KL | 311-10KGRCT-ND | Resistors_SMD:R_0603_HandSoldering
R39 | 10k | RC0603JR-0710KL | 311-10KGRCT-ND | Resistors_SMD:R_0603_HandSoldering
R40 | 50 |  |  | Resistors_SMD:R_0805
R41 | 39 | RC0603FR-0739RL | 311-39.0HRTR-ND | Resistors_SMD:R_0603
R42 | 39 | RC0603FR-0739RL | 311-39.0HRTR-ND | Resistors_SMD:R_0603
R43 | 470 | RC0603FR-07470RL | 311-470HRCT-ND | Resistors_SMD:R_0603
R44 | 3.3k |  |  | Capacitors_SMD:C_0805
R45 | 39 | RC0603FR-0739RL | 311-39.0HRTR-ND | Resistors_SMD:R_0603
R46 | 39 | RC0603FR-0739RL | 311-39.0HRTR-ND | Resistors_SMD:R_0603
R47 | 470 | RC0402FR-07470RL | 311-470LRCT-ND | Resistors_SMD:R_0402
R48 | 1k |  |  | Capacitors_SMD:C_0805
R49 | 1k |  |  | Capacitors_SMD:C_0805
R50 | 1k |  |  | Resistors_SMD:R_0805
R51 | 200 |  |  | Resistors_SMD:R_0805
R52 | 82.5 | RC0603FR-0782R5L | 311-82.5HRCT-ND | Resistors_SMD:R_0603
R53 | 124 | RC0603FR-07124RL | 311-124HRCT-ND | Resistors_SMD:R_0603
R54 | 82.5 | RC0603FR-0782R5L | 311-82.5HRCT-ND | Resistors_SMD:R_0603
R55 | 124 | RC0603FR-07124RL | 311-124HRCT-ND | Resistors_SMD:R_0603
R56 | 7.15k |  |  | Resistors_SMD:R_0805
R57 | 7.15k |  |  | Resistors_SMD:R_0805
R58 | 7.15k |  |  | Resistors_SMD:R_0805
R59 | 7.15k |  |  | Resistors_SMD:R_0805
R60 | 50 |  |  | Resistors_SMD:R_0805
R61 | 50 |  |  | Resistors_SMD:R_0805
R62 | 50 |  |  | Resistors_SMD:R_0805
R63 | 39 | RC0603FR-0739RL | 311-39.0HRTR-ND | Resistors_SMD:R_0603
R64 | 39 | RC0603FR-0739RL | 311-39.0HRTR-ND | Resistors_SMD:R_0603
R65 | 470 | RC0603FR-07470RL | 311-470HRCT-ND | Resistors_SMD:R_0603
R66 | 3.3k |  |  | Capacitors_SMD:C_0805
R67 | 39 | RC0603FR-0739RL | 311-39.0HRTR-ND | Resistors_SMD:R_0603
R68 | 39 | RC0603FR-0739RL | 311-39.0HRTR-ND | Resistors_SMD:R_0603
R69 | 470 | RC0402FR-07470RL | 311-470LRCT-ND | Resistors_SMD:R_0402
R70 | 1k |  |  | Capacitors_SMD:C_0805
R71 | 50 |  |  | Resistors_SMD:R_0805
R72 | 50 |  |  | Resistors_SMD:R_0805
R73 | 39 | RC0603FR-0739RL | 311-39.0HRTR-ND | Resistors_SMD:R_0603
R74 | 39 | RC0603FR-0739RL | 311-39.0HRTR-ND | Resistors_SMD:R_0603
R75 | 470 | RC0603FR-07470RL | 311-470HRCT-ND | Resistors_SMD:R_0603
R76 | 3.3k |  |  | Capacitors_SMD:C_0805
R77 | 39 | RC0603FR-0739RL | 311-39.0HRTR-ND | Resistors_SMD:R_0603
R78 | 39 | RC0603FR-0739RL | 311-39.0HRTR-ND | Resistors_SMD:R_0603
R79 | 470 | RC402FR-07402RL | YAG3125CT-ND | Resistors_SMD:R_0402
R80 | 1k |  |  | Capacitors_SMD:C_0805
R81 | 6.8k |  |  | Resistors_SMD:R_0805
R82 | 1k |  |  | Resistors_SMD:R_0805
R83 | 200 |  |  | Resistors_SMD:R_0805
R84 | 82.5 | RC0603FR-0782R5L | 311-82.5HRCT-ND | Resistors_SMD:R_0603
R85 | 124 | RC0603FR-07124RL | 311-124HRCT-ND | Resistors_SMD:R_0603
R86 | 82.5 | RC0603FR-0782R5L | 311-82.5HRCT-ND | Resistors_SMD:R_0603
R87 | 124 | RC0603FR-07124RL | 311-124HRCT-ND | Resistors_SMD:R_0603
R88 | 6.8k |  |  | Resistors_SMD:R_0805
R89 | 1k |  |  | Resistors_SMD:R_0805
R90 | 200 |  |  | Resistors_SMD:R_0805
R91 | 82.5 | RC0603FR-0782R5L | 311-82.5HRCT-ND | Resistors_SMD:R_0603
R92 | 124 | RC0603FR-07124RL | 311-124HRCT-ND | Resistors_SMD:R_0603
R93 | 82.5 | RC0603FR-0782R5L | 311-82.5HRCT-ND | Resistors_SMD:R_0603
R94 | 124 | RC0603FR-07124RL | 311-124HRCT-ND | Resistors_SMD:R_0603
R95 | 50 |  |  | Resistors_SMD:R_0805
R96 | 50 |  |  | Resistors_SMD:R_0805
R97 | 50 |  |  | Resistors_SMD:R_0805
R98 | 50 |  |  | Resistors_SMD:R_0805
R99 | 1k |  |  | Resistors_SMD:R_0805
R100 | 1k |  |  | Resistors_SMD:R_0805
R101 | 4.5k |  |  | Resistors_SMD:R_0805
R102 | 1k |  |  | Resistors_SMD:R_0805
R103 | 1k |  |  | Resistors_SMD:R_0805
R104 | 1k |  |  | Resistors_SMD:R_0805
R105 | 124 | RC0603FR-07124RL | 311-124HRCT-ND | Resistors_SMD:R_0603
R106 | 124 | RC0603FR-07124RL | 311-124HRCT-ND | Resistors_SMD:R_0603
R107 | 124 | RC0603FR-07124RL | 311-124HRCT-ND | Resistors_SMD:R_0603
R108 | 124 | RC0603FR-07124RL | 311-124HRCT-ND | Resistors_SMD:R_0603
R109 | 1k |  |  | Resistors_SMD:R_0805
R110 | 1k |  |  | Resistors_SMD:R_0805
R111 | 1k |  |  | Resistors_SMD:R_0805
R112 | 1k |  |  | Resistors_SMD:R_0805
RV1 | 10k | 3266W-1-103LF | 3266W-103LF-ND | Potentiometers:Potentiometer_Trimmer_Bourns_3266W
RV2 | 50k | 3266W-1-503LF | 3266W-503LF-ND | Potentiometers:Potentiometer_Trimmer_Bourns_3266W
RV3 | 10k | 3266W-1-103LF | 3266W-103LF-ND | Potentiometers:Potentiometer_Trimmer_Bourns_3266W
RV4 | 10k | 3266W-1-103LF | 3266W-103LF-ND | Potentiometers:Potentiometer_Trimmer_Bourns_3266W
RV5 | 10k | 3266W-1-103LF | 3266W-103LF-ND | Potentiometers:Potentiometer_Trimmer_Bourns_3266W
RV6 | 10k | 3266W-1-103LF | 3266W-103LF-ND | Potentiometers:Potentiometer_Trimmer_Bourns_3266W
RV7 | 10k | 3266W-1-103LF | 3266W-103LF-ND | Potentiometers:Potentiometer_Trimmer_Bourns_3266W
RV8 | 50k | 3266W-1-503LF | 3266W-503LF-ND | Potentiometers:Potentiometer_Trimmer_Bourns_3266W
RV9 | 10k | 3266W-1-103LF | 3266W-103LF-ND | Potentiometers:Potentiometer_Trimmer_Bourns_3266W
RV10 | 10k | 3266W-1-103LF | 3266W-103LF-ND | Potentiometers:Potentiometer_Trimmer_Bourns_3266W
RV11 | 50k | 3266W-1-503LF | 3266W-503LF-ND | Potentiometers:Potentiometer_Trimmer_Bourns_3266W
RV12 | 10k | 3266W-1-103LF | 3266W-103LF-ND | Potentiometers:Potentiometer_Trimmer_Bourns_3266W
RV13 | 50k | 3266W-1-503LF | 3266W-503LF-ND | Potentiometers:Potentiometer_Trimmer_Bourns_3266W
RV14 | 10k | 3266W-1-103LF | 3266W-103LF-ND | Potentiometers:Potentiometer_Trimmer_Bourns_3266W
RV15 | 10k | 3266W-1-103LF | 3266W-103LF-ND | Potentiometers:Potentiometer_Trimmer_Bourns_3266W

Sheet: Capacitors
Ref | Value | MPN | DK | Footprint
C1 | 330u | ECA-1HM331 | P5184-ND | Capacitors_THT:CP_Radial_D10.0mm_P5.00mm
C2 | 330u | ECA-1HM331 | P5184-ND | Capacitors_THT:CP_Radial_D10.0mm_P5.00mm
C3 | 4.7u | UMK316ABJ475KD-T | 587-2988-1-ND | Capacitors_SMD:C_1206_HandSoldering
C4 | 100u | UVz1H101MPD1TD | 493-13464-1-ND | Capacitors_THT:CP_Radial_D8.0mm_P3.50mm
C5 | 4.7u | UMK316ABJ475KD-T | 587-2988-1-ND | Capacitors_SMD:C_1206_HandSoldering
C6 | 100u | EEU-FM1H101B | P19712CT-ND | Capacitors_THT:CP_Radial_D8.0mm_P5.00mm
C7 | 100u | EEU-FM1H101B | P19712CT-ND | Capacitors_THT:CP_Radial_D8.0mm_P5.00mm
C8 | 100u | EEU-FM1H101B | P19712CT-ND | Capacitors_THT:CP_Radial_D8.0mm_P5.00mm
C9 | 100u | EEU-FM1H101B | P19712CT-ND | Capacitors_THT:CP_Radial_D8.0mm_P5.00mm
C10 | 100u | C3216X5R1A107M160AC | 445-6007-2-ND | Capacitors_SMD:C_1206_HandSoldering
C11 | 100u | C3216X5R1A107M160AC | 445-6007-2-ND | Capacitors_SMD:C_1206_HandSoldering
C12 | 100u | C3216X5R1A107M160AC | 445-6007-2-ND | Capacitors_SMD:C_1206_HandSoldering
C13 | 100u | C3216X5R1A107M160AC | 445-6007-2-ND | Capacitors_SMD:C_1206_HandSoldering
C14 | 1n | 202R18W102KV4E | 709-1036-1-ND | Resistors_SMD:R_1206_HandSoldering
C15 | 10u | C0805C106K8PACTU | 399-4925-2-ND | Capacitors_SMD:C_0805_HandSoldering
C16 | 10u | C0805C106K8PACTU | 399-4925-2-ND | Capacitors_SMD:C_0805_HandSoldering
C17 | 10u | C0805C106K8PACTU | 399-4925-2-ND | Capacitors_SMD:C_0805_HandSoldering
C18 | 10u | C0805C106K8PACTU | 399-4925-2-ND | Capacitors_SMD:C_0805_HandSoldering
C19 | 12u | UPW1V120MDD1TP | 493-11380-1-ND | Capacitors_THT:C_Radial_D5_L11_P2
C20 | 100u | UVz1H101MPD1TD | 493-13464-1-ND | Capacitors_THT:CP_Radial_D8.0mm_P3.50mm
C21 | 620p | C1206C621G5GACTU | 399-9371-1-ND | Capacitors_SMD:C_1206
C22 | 620p | C1206C621G5GACTU | 399-9371-1-ND | Capacitors_SMD:C_1206
C23 | 2.2u | GRM155R61C225KE11DDDD | 490-10695-1-ND | Capacitors_SMD:C_0402
C24 | 2.2u | GRM155R61C225KE11DDDD | 490-10695-1-ND | Capacitors_SMD:C_0402
C25 | 2.2n | LLL185R71H222MA01 | 490-4311-1-ND | Capacitors_SMD:C_0306
C26 | 2.2n | LLL185R71H222MA01 | 490-4311-1-ND | Capacitors_SMD:C_0306
C27 | 2.2n | LLL185R71H222MA01 | 490-4311-1-ND | Capacitors_SMD:C_0306
C28 | 2.2n | LLL185R71H222MA01 | 490-4311-1-ND | Capacitors_SMD:C_0306
C29 | 30p | C0603C300J5GACTU | 399-9057-1-ND | Capacitors_SMD:C_0603
C30 | 2.2u | GRM155R61C225KE11DDDD | 490-10695-1-ND | Capacitors_SMD:C_0402
C31 | 2.2u | GRM155R61C225KE11DDDD | 490-10695-1-ND | Capacitors_SMD:C_0402
C32 | 2.2n | LLL185R71H222MA01 | 490-4311-1-ND | Capacitors_SMD:C_0306
C33 | 2.2n | LLL185R71H222MA01 | 490-4311-1-ND | Capacitors_SMD:C_0306
C34 | 2.2n | LLL185R71H222MA01 | 490-4311-1-ND | Capacitors_SMD:C_0306
C35 | 2.2n | LLL185R71H222MA01 | 490-4311-1-ND | Capacitors_SMD:C_0306
C36 | 2.2n | LLL185R71H222MA01 | 490-4311-1-ND | Capacitors_SMD:C_0306
C37 | 1u | Any >10V |  | Capacitors_SMD:C_0603
C38 | 2.2u | GRM155R61C225KE11DDDD | 490-10695-1-ND | Capacitors_SMD:C_0402
C39 | 2.2u | GRM155R61C225KE11DDDD | 490-10695-1-ND | Capacitors_SMD:C_0402
C40 | 2.2n | LLL185R71H222MA01 | 490-4311-1-ND | Capacitors_SMD:C_0306
C41 | 2.2n | LLL185R71H222MA01 | 490-4311-1-ND | Capacitors_SMD:C_0306
C42 | 30p | 06031A430FAT2A | 478-10205-1-ND | Capacitors_SMD:C_0603
C43 | 2.2n | LLL185R71H222MA01 | 490-4311-1-ND | Capacitors_SMD:C_0306
C44 | 2.2n | LLL185R71H222MA01 | 490-4311-1-ND | Capacitors_SMD:C_0306
C45 | 2.2u | GRM155R61C225KE11DDDD | 490-10695-1-ND | Capacitors_SMD:C_0402
C46 | 2.2u | GRM155R61C225KE11DDDD | 490-10695-1-ND | Capacitors_SMD:C_0402
C47 | 2.2u | GRM155R61C225KE11DDDD | 490-10695-1-ND | Capacitors_SMD:C_0402
C48 | 100p | C0603C101J5GACTU | 399-1061-1-ND | Capacitors_SMD:C_0603
C49 | 2.2n | LLL185R71H222MA01 | 490-4311-1-ND | Capacitors_SMD:C_0306
C50 | 2.2n | LLL185R71H222MA01 | 490-4311-1-ND | Capacitors_SMD:C_0306
C51 | 2.2n | LLL185R71H222MA01 | 490-4311-1-ND | Capacitors_SMD:C_0306
C52 | 2.2n | LLL185R71H222MA01 | 490-4311-1-ND | Capacitors_SMD:C_0306
C53 | 47u | Any >10V |  | Resistors_SMD:R_0805_HandSoldering
C54 | 100n | Any >10V |  | Capacitors_SMD:C_0603
C55 | 10u | LLL31MR70J475MA01L | 490-4392-1-ND | Resistors_SMD:R_0612
C56 | 10u | LLL31MR70J475MA01L | 490-4392-1-ND | Resistors_SMD:R_0612
C57 | 47u | Any >10V |  | Resistors_SMD:R_0805_HandSoldering
C58 | 10u | LLL31MR70J475MA01L | 490-4392-1-ND | Resistors_SMD:R_0612
C59 | 10u | LLL31MR70J475MA01L | 490-4392-1-ND | Resistors_SMD:R_0612
C60 | 10u | LLL31MR70J475MA01L | 490-4392-1-ND | Resistors_SMD:R_0612
C61 | 100p | C0603C101J5GACTU | 399-1061-1-ND | Capacitors_SMD:C_0603
C62 | 10u | LLL31MR70J475MA01L | 490-4392-1-ND | Resistors_SMD:R_0612
C63 | 10u | LLL31MR70J475MA01L | 490-4392-1-ND | Resistors_SMD:R_0612
C64 | 2.2u | GRM155R61C225KE11DDDD | 490-10695-1-ND | Capacitors_SMD:C_0402_NoSilk
C65 | 1n | Any >6.3V |  | Capacitors_SMD:C_0805_HandSoldering
C66 | 1n | Any >6.3V |  | Capacitors_SMD:C_0805_HandSoldering
C67 | 1n | Any >6.3V |  | Capacitors_SMD:C_0805_HandSoldering
C68 | 1n | Any >6.3V |  | Capacitors_SMD:C_0805_HandSoldering
C69 | 1u | Any >6.3V |  | Capacitors_SMD:C_0603_HandSoldering
C70 | 1u | Any >6.3V |  | Capacitors_SMD:C_0603_HandSoldering
C71 | 1u | Any >6.3V |  | Capacitors_SMD:C_0603_HandSoldering
C72 | 1u | Any >6.3V |  | Capacitors_SMD:C_0603_HandSoldering
C73 | 1u | Any >6.3V |  | Capacitors_SMD:C_0603_HandSoldering
C74 | 1u | Any >6.3V |  | Capacitors_SMD:C_0603_HandSoldering
C75 | 620p | C1206C621G5GACTU | 399-9371-1-ND | Capacitors_SMD:C_1206
C76 | 2.2u | GRM155R61C225KE11DDDD | 490-10695-1-ND | Capacitors_SMD:C_0402
C77 | 2.2u | GRM155R61C225KE11DDDD | 490-10695-1-ND | Capacitors_SMD:C_0402
C78 | 2.2u | GRM155R61C225KE11DDDD | 490-10695-1-ND | Capacitors_SMD:C_0402
C79 | 2.2n | LLL185R71H222MA01 | 490-4311-1-ND | Capacitors_SMD:C_0306
C80 | 2.2n | LLL185R71H222MA01 | 490-4311-1-ND | Capacitors_SMD:C_0306
C81 | 2.2n | LLL185R71H222MA01 | 490-4311-1-ND | Capacitors_SMD:C_0306
C82 | 2.2n | LLL185R71H222MA01 | 490-4311-1-ND | Capacitors_SMD:C_0306
C83 | 30p | GRM0335C1H300JA01D | 490-11324-1-ND | Capacitors_SMD:C_0603
C84 | 2.2u | GRM155R61C225KE11DDDD | 490-10695-1-ND | Capacitors_SMD:C_0402
C85 | 2.2u | GRM155R61C225KE11DDDD | 490-10695-1-ND | Capacitors_SMD:C_0402
C86 | 2.2n | LLL185R71H222MA01 | 490-4311-1-ND | Capacitors_SMD:C_0306
C87 | 2.2n | LLL185R71H222MA01 | 490-4311-1-ND | Capacitors_SMD:C_0306
C88 | 2.2n | LLL185R71H222MA01 | 490-4311-1-ND | Capacitors_SMD:C_0306
C89 | 2.2n | LLL185R71H222MA01 | 490-4311-1-ND | Capacitors_SMD:C_0306
C90 | 2.2n | LLL185R71H222MA01 | 490-4311-1-ND | Capacitors_SMD:C_0306
C91 | 1u | Any >10V |  | Capacitors_SMD:C_0603
C92 | 2.2u | GRM155R61C225KE11DDDD | 490-10695-1-ND | Capacitors_SMD:C_0402
C93 | 2.2u | GRM155R61C225KE11DDDD | 490-10695-1-ND | Capacitors_SMD:C_0402
C94 | 2.2n | LLL185R71H222MA01 | 490-4311-1-ND | Capacitors_SMD:C_0306
C95 | 2.2n | LLL185R71H222MA01 | 490-4311-1-ND | Capacitors_SMD:C_0306
C96 | 30p | GRM0335C1H300JA01D | 490-11324-1-ND | Capacitors_SMD:C_0603
C97 | 2.2n | LLL185R71H222MA01 | 490-4311-1-ND | Capacitors_SMD:C_0306
C98 | 2.2n | LLL185R71H222MA01 | 490-4311-1-ND | Capacitors_SMD:C_0306
C99 | 2.2u | GRM155R61C225KE11DDDD | 490-10695-1-ND | Capacitors_SMD:C_0402
C100 | 2.2u | GRM155R61C225KE11DDDD | 490-10695-1-ND | Capacitors_SMD:C_0402
C101 | 2.2u | GRM155R61C225KE11DDDD | 490-10695-1-ND | Capacitors_SMD:C_0402
C102 | 100p | C0603C101J5GACTU | 399-1061-1-ND | Capacitors_SMD:C_0603
C103 | 2.2n | LLL185R71H222MA01 | 490-4311-1-ND | Capacitors_SMD:C_0306
C104 | 2.2n | LLL185R71H222MA01 | 490-4311-1-ND | Capacitors_SMD:C_0306
C105 | 2.2n | LLL185R71H222MA01 | 490-4311-1-ND | Capacitors_SMD:C_0306
C106 | 2.2n | LLL185R71H222MA01 | 490-4311-1-ND | Capacitors_SMD:C_0306
C107 | 2.2u | GRM155R61C225KE11DDDD | 490-10695-1-ND | Capacitors_SMD:C_0402
C108 | 2.2u | GRM155R61C225KE11DDDD | 490-10695-1-ND | Capacitors_SMD:C_0402
C109 | 2.2n | LLL185R71H222MA01 | 490-4311-1-ND | Capacitors_SMD:C_0306
C110 | 2.2n | LLL185R71H222MA01 | 490-4311-1-ND | Capacitors_SMD:C_0306
C111 | 2.2n | LLL185R71H222MA01 | 490-4311-1-ND | Capacitors_SMD:C_0306
C112 | 2.2n | LLL185R71H222MA01 | 490-4311-1-ND | Capacitors_SMD:C_0306
C113 | 2.2u | GRM155R61C225KE11DDDD | 490-10695-1-ND | Capacitors_SMD:C_0402
C114 | 2.2u | GRM155R61C225KE11DDDD | 490-10695-1-ND | Capacitors_SMD:C_0402
C115 | 2.2n | LLL185R71H222MA01 | 490-4311-1-ND | Capacitors_SMD:C_0306
C116 | 2.2n | LLL185R71H222MA01 | 490-4311-1-ND | Capacitors_SMD:C_0306
C117 | 2.2n | LLL185R71H222MA01 | 490-4311-1-ND | Capacitors_SMD:C_0306
C118 | 2.2n | LLL185R71H222MA01 | 490-4311-1-ND | Capacitors_SMD:C_0306
C119 | 47u | Any >10V |  | Resistors_SMD:R_0805_HandSoldering
C120 | 100n | Any >10V |  | Capacitors_SMD:C_0603
C121 | 10u | LLL31MR70J475MA01L | 490-4392-1-ND | Resistors_SMD:R_0612
C122 | 10u | LLL31MR70J475MA01L | 490-4392-1-ND | Resistors_SMD:R_0612
C123 | 47u | Any >10V |  | Resistors_SMD:R_0805_HandSoldering
C124 | 10u | LLL31MR70J475MA01L | 490-4392-1-ND | Resistors_SMD:R_0612
C125 | 10u | LLL31MR70J475MA01L | 490-4392-1-ND | Resistors_SMD:R_0612
C126 | 10u | LLL31MR70J475MA01L | 490-4392-1-ND | Resistors_SMD:R_0612
C127 | 100p | C0603C101J5GACTU | 399-1061-1-ND | Capacitors_SMD:C_0603
C128 | 10u | LLL31MR70J475MA01L | 490-4392-1-ND | Resistors_SMD:R_0612
C129 | 10u | LLL31MR70J475MA01L | 490-4392-1-ND | Resistors_SMD:R_0612
C130 | 2.2u | GRM155R61C225KE11DDDD | 490-10695-1-ND | Capacitors_SMD:C_0402_NoSilk
C131 | 2.2u | GRM155R61C225KE11DDDD | 490-10695-1-ND | Capacitors_SMD:C_0402
C132 | 2.2n | LLL185R71H222MA01 | 490-4311-1-ND | Capacitors_SMD:C_0306
C133 | 2.2n | LLL185R71H222MA01 | 490-4311-1-ND | Capacitors_SMD:C_0306
C134 | 2.2n | LLL185R71H222MA01 | 490-4311-1-ND | Capacitors_SMD:C_0306
C135 | 2.2n | LLL185R71H222MA01 | 490-4311-1-ND | Capacitors_SMD:C_0306
C136 | 30p | C0603C300J5GACTU | 399-9057-1-ND | Capacitors_SMD:C_0603
C137 | 2.2u | GRM155R61C225KE11DDDD | 490-10695-1-ND | Capacitors_SMD:C_0402
C138 | 2.2u | GRM155R61C225KE11DDDD | 490-10695-1-ND | Capacitors_SMD:C_0402
C139 | 2.2n | LLL185R71H222MA01 | 490-4311-1-ND | Capacitors_SMD:C_0306
C140 | 2.2n | LLL185R71H222MA01 | 490-4311-1-ND | Capacitors_SMD:C_0306
C141 | 2.2n | LLL185R71H222MA01 | 490-4311-1-ND | Capacitors_SMD:C_0306
C142 | 2.2n | LLL185R71H222MA01 | 490-4311-1-ND | Capacitors_SMD:C_0306
C143 | 2.2n | LLL185R71H222MA01 | 490-4311-1-ND | Capacitors_SMD:C_0306
C144 | 1u | Any >10V |  | Capacitors_SMD:C_0603
C145 | 2.2u | GRM155R61C225KE11DDDD | 490-10695-1-ND | Capacitors_SMD:C_0402
C146 | 2.2u | GRM155R61C225KE11DDDD | 490-10695-1-ND | Capacitors_SMD:C_0402
C147 | 2.2n | LLL185R71H222MA01 | 490-4311-1-ND | Capacitors_SMD:C_0306
C148 | 2.2n | LLL185R71H222MA01 | 490-4311-1-ND | Capacitors_SMD:C_0306
C149 | 30p | 06031A430FAT2A | 478-10205-1-ND | Capacitors_SMD:C_0603
C150 | 2.2n | LLL185R71H222MA01 | 490-4311-1-ND | Capacitors_SMD:C_0306
C151 | 2.2n | LLL185R71H222MA01 | 490-4311-1-ND | Capacitors_SMD:C_0306
C152 | 2.2u | GRM155R61C225KE11DDDD | 490-10695-1-ND | Capacitors_SMD:C_0402
C153 | 2.2u | GRM155R61C225KE11DDDD | 490-10695-1-ND | Capacitors_SMD:C_0402
C154 | 2.2u | GRM155R61C225KE11DDDD | 490-10695-1-ND | Capacitors_SMD:C_0402
C155 | 100p | C0603C101J5GACTU | 399-1061-1-ND | Capacitors_SMD:C_0603
C156 | 2.2n | LLL185R71H222MA01 | 490-4311-1-ND | Capacitors_SMD:C_0306
C157 | 2.2n | LLL185R71H222MA01 | 490-4311-1-ND | Capacitors_SMD:C_0306
C158 | 2.2n | LLL185R71H222MA01 | 490-4311-1-ND | Capacitors_SMD:C_0306
C159 | 2.2n | LLL185R71H222MA01 | 490-4311-1-ND | Capacitors_SMD:C_0306
C160 | 2.2u | GRM155R61C225KE11DDDD | 490-10695-1-ND | Capacitors_SMD:C_0402
C161 | 2.2u | GRM155R61C225KE11DDDD | 490-10695-1-ND | Capacitors_SMD:C_0402
C162 | 2.2n | LLL185R71H222MA01 | 490-4311-1-ND | Capacitors_SMD:C_0306
C163 | 2.2n | LLL185R71H222MA01 | 490-4311-1-ND | Capacitors_SMD:C_0306
C164 | 2.2n | LLL185R71H222MA01 | 490-4311-1-ND | Capacitors_SMD:C_0306
C165 | 2.2n | LLL185R71H222MA01 | 490-4311-1-ND | Capacitors_SMD:C_0306
C166 | 2.2u | GRM155R61C225KE11DDDD | 490-10695-1-ND | Capacitors_SMD:C_0402
C167 | 2.2u | GRM155R61C225KE11DDDD | 490-10695-1-ND | Capacitors_SMD:C_0402
C168 | 2.2n | LLL185R71H222MA01 | 490-4311-1-ND | Capacitors_SMD:C_0306
C169 | 2.2n | LLL185R71H222MA01 | 490-4311-1-ND | Capacitors_SMD:C_0306
C170 | 2.2n | LLL185R71H222MA01 | 490-4311-1-ND | Capacitors_SMD:C_0306
C171 | 2.2n | LLL185R71H222MA01 | 490-4311-1-ND | Capacitors_SMD:C_0306
C172 | 30p | C0603C300J5GACTU | 399-9057-1-ND | Capacitors_SMD:C_0603
C173 | 2.2u | GRM155R61C225KE11DDDD | 490-10695-1-ND | Capacitors_SMD:C_0402
C174 | 2.2u | GRM155R61C225KE11DDDD | 490-10695-1-ND | Capacitors_SMD:C_0402
C175 | 2.2n | LLL185R71H222MA01 | 490-4311-1-ND | Capacitors_SMD:C_0306
C176 | 2.2n | LLL185R71H222MA01 | 490-4311-1-ND | Capacitors_SMD:C_0306
C177 | 2.2n | LLL185R71H222MA01 | 490-4311-1-ND | Capacitors_SMD:C_0306
C178 | 2.2n | LLL185R71H222MA01 | 490-4311-1-ND | Capacitors_SMD:C_0306
C179 | 2.2n | LLL185R71H222MA01 | 490-4311-1-ND | Capacitors_SMD:C_0306
C180 | 1u | Any >10V |  | Capacitors_SMD:C_0603
C181 | 2.2u | GRM155R61C225KE11DDDD | 490-10695-1-ND | Capacitors_SMD:C_0402
C182 | 2.2u | GRM155R61C225KE11DDDD | 490-10695-1-ND | Capacitors_SMD:C_0402
C183 | 2.2n | LLL185R71H222MA01 | 490-4311-1-ND | Capacitors_SMD:C_0306
C184 | 2.2n | LLL185R71H222MA01 | 490-4311-1-ND | Capacitors_SMD:C_0306
C185 | 30p | 06031A430FAT2A | 478-10205-1-ND | Capacitors_SMD:C_0603
C186 | 2.2n | LLL185R71H222MA01 | 490-4311-1-ND | Capacitors_SMD:C_0306
C187 | 2.2n | LLL185R71H222MA01 | 490-4311-1-ND | Capacitors_SMD:C_0306
C188 | 2.2u | GRM155R61C225KE11DDDD | 490-10695-1-ND | Capacitors_SMD:C_0402
C189 | 2.2u | GRM155R61C225KE11DDDD | 490-10695-1-ND | Capacitors_SMD:C_0402
C190 | 2.2u | GRM155R61C225KE11DDDD | 490-10695-1-ND | Capacitors_SMD:C_0402
C191 | 100p | C0603C101J5GACTU | 399-1061-1-ND | Capacitors_SMD:C_0603
C192 | 2.2n | LLL185R71H222MA01 | 490-4311-1-ND | Capacitors_SMD:C_0306
C193 | 2.2n | LLL185R71H222MA01 | 490-4311-1-ND | Capacitors_SMD:C_0306
C194 | 2.2n | LLL185R71H222MA01 | 490-4311-1-ND | Capacitors_SMD:C_0306
C195 | 2.2n | LLL185R71H222MA01 | 490-4311-1-ND | Capacitors_SMD:C_0306
C196 | 2.2u | GRM155R61C225KE11DDDD | 490-10695-1-ND | Capacitors_SMD:C_0402
C197 | 2.2u | GRM155R61C225KE11DDDD | 490-10695-1-ND | Capacitors_SMD:C_0402
C198 | 2.2n | LLL185R71H222MA01 | 490-4311-1-ND | Capacitors_SMD:C_0306
C199 | 2.2n | LLL185R71H222MA01 | 490-4311-1-ND | Capacitors_SMD:C_0306
C200 | 2.2n | LLL185R71H222MA01 | 490-4311-1-ND | Capacitors_SMD:C_0306
C201 | 2.2n | LLL185R71H222MA01 | 490-4311-1-ND | Capacitors_SMD:C_0306
C202 | 47u | Any >10V |  | Resistors_SMD:R_0805_HandSoldering
C203 | 100n | Any >10V |  | Capacitors_SMD:C_0603
C204 | 10u | LLL31MR70J475MA01L | 490-4392-1-ND | Resistors_SMD:R_0612
C205 | 10u | LLL31MR70J475MA01L | 490-4392-1-ND | Resistors_SMD:R_0612
C206 | 47u |  |  | Resistors_SMD:R_0805_HandSoldering
C207 | 10u | LLL31MR70J475MA01L | 490-4392-1-ND | Resistors_SMD:R_0612
C208 | 10u | LLL31MR70J475MA01L | 490-4392-1-ND | Resistors_SMD:R_0612
C209 | 10u | LLL31MR70J475MA01L | 490-4392-1-ND | Resistors_SMD:R_0612
C210 | 100p | C0603C101J5GACTU | 399-1061-1-ND | Capacitors_SMD:C_0603
C211 | 10u | LLL31MR70J475MA01L | 490-4392-1-ND | Resistors_SMD:R_0612
C212 | 10u | LLL31MR70J475MA01L | 490-4392-1-ND | Resistors_SMD:R_0612
C213 | 2.2u | GRM155R61C225KE11DDDD | 490-10695-1-ND | Capacitors_SMD:C_0402_NoSilk
C214 | 47u | Any >10V |  | Resistors_SMD:R_0805_HandSoldering
C215 | 100n | Any >10V |  | Capacitors_SMD:C_0603
C216 | 10u | LLL31MR70J475MA01L | 490-4392-1-ND | Resistors_SMD:R_0612
C217 | 10u | LLL31MR70J475MA01L | 490-4392-1-ND | Resistors_SMD:R_0612
C218 | 47u | Any >10V |  | Resistors_SMD:R_0805_HandSoldering
C219 | 10u | LLL31MR70J475MA01L | 490-4392-1-ND | Resistors_SMD:R_0612
C220 | 10u | LLL31MR70J475MA01L | 490-4392-1-ND | Resistors_SMD:R_0612
C221 | 10u | LLL31MR70J475MA01L | 490-4392-1-ND | Resistors_SMD:R_0612
C222 | 100p | C0603C101J5GACTU | 399-1061-1-ND | Capacitors_SMD:C_0603
C223 | 10u | LLL31MR70J475MA01L | 490-4392-1-ND | Resistors_SMD:R_0612
C224 | 10u | LLL31MR70J475MA01L | 490-4392-1-ND | Resistors_SMD:R_0612
C225 | 2.2u | GRM155R61C225KE11DDDD | 490-10695-1-ND | Capacitors_SMD:C_0402_NoSilk
C226 | 1u | Any >6.3V |  | Capacitors_SMD:C_0603_HandSoldering
C227 | 1u | Any >6.3V |  | Capacitors_SMD:C_0603_HandSoldering
C228 | 1u | Any >6.3V |  | Capacitors_SMD:C_0603_HandSoldering
C229 | Unknown. Leave unpopulated. |  |  | Capacitors_SMD:C_0805
C230 | Unknown. Leave unpopulated. |  |  | Capacitors_SMD:C_0805
C231 | 2.2u | GRM155R61C225KE11DDDD | 490-10695-1-ND | Capacitors_SMD:C_0402_NoSilk
C232 | 2.2u | GRM155R61C225KE11DDDD | 490-10695-1-ND | Capacitors_SMD:C_0402_NoSilk
C233 | 2.2u | GRM155R61C225KE11DDDD | 490-10695-1-ND | Capacitors_SMD:C_0402_NoSilk
C234 | 2.2u | GRM155R61C225KE11DDDD | 490-10695-1-ND | Capacitors_SMD:C_0402_NoSilk

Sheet: Inductors
Ref | Value | MPN | DK | Footprint
L1 | 56u | 2210-V-RC | M8872-ND | Inductors_THT:L_Toroid_Vertical_L22.4mm_W10.2mm_P7.90mm_Vishay_TJ4
L2 | 12u | RLB0914-120KL | RLB0914-120KL-ND | Inductors_THT:L_Radial_D10.0mm_P5.00mm_Fastron_07M
L3 | 12u | AIUR-07-120K | AIUR-07-120K-ND | Inductors_THT:L_Radial_D6.0mm_P4.00mm
L4 | 3u | 74475 | 732-7146-ND | Inductors_THT:L_Radial_D12.0mm_P6.5mm
L5 | 3u | 74475 | 732-7146-ND | Inductors_THT:L_Radial_D12.0mm_P6.5mm
L6 | 1k@100MHz | FB MH3225HM601NT | 587-1755-1-ND | Inductors_SMD:L_1210
L7 | 1k@100MHz | FB MH3225HM601NT | 587-1755-1-ND | Inductors_SMD:L_1210
L8 | 1k@100MHz | FB MH3225HM601NT | 587-1755-1-ND | Inductors_SMD:L_1210
L9 | 1k@100MHz | FB MH3225HM601NT | 587-1755-1-ND | Inductors_SMD:L_1210
L10 | 1k@100MHz | FB MH3225HM601NT | 587-1755-1-ND | Inductors_SMD:L_1210
L11 | 1k@100MHz | FB MH3225HM601NT | 587-1755-1-ND | Inductors_SMD:L_1210
L12 | 1k@100MHz | FB MH3225HM601NT | 587-1755-1-ND | Inductors_SMD:L_1210
L13 | 1k@100MHz | FB MH3225HM601NT | 587-1755-1-ND | Inductors_SMD:L_1210
L14 | 1k@100MHz | FB MH3225HM601NT | 587-1755-1-ND | Inductors_SMD:L_1210
L15 | 1k@100MHz | FB MH3225HM601NT | 587-1755-1-ND | Inductors_SMD:L_1210
L16 | 1k@100MHz | FB MH3225HM601NT | 587-1755-1-ND | Inductors_SMD:L_1210
L17 | 1k@100MHz | FB MH3225HM601NT | 587-1755-1-ND | Inductors_SMD:L_1210
L18 | 1k@100MHz | FB MH3225HM601NT | 587-1755-1-ND | Inductors_SMD:L_1210
L19 | 1k@100MHz | FB MH3225HM601NT | 587-1755-1-ND | Inductors_SMD:L_1210
L20 | 1k@100MHz | FB MH3225HM601NT | 587-1755-1-ND | Inductors_SMD:L_1210
L21 | 1k@100MHz | FB MH3225HM601NT | 587-1755-1-ND | Inductors_SMD:L_1210
L22 | 1k@100MHz | FB MH3225HM601NT | 587-1755-1-ND | Inductors_SMD:L_1210
L23 | 1k@100MHz | FB MH3225HM601NT | 587-1755-1-ND | Inductors_SMD:L_1210
L24 | 1k@100MHz | FB MH3225HM601NT | 587-1755-1-ND | Inductors_SMD:L_1210
L25 | 1k@100MHz | FB MH3225HM601NT | 587-1755-1-ND | Inductors_SMD:L_1210
L26 | 1k@100MHz | FB MH3225HM601NT | 587-1755-1-ND | Inductors_SMD:L_1210
L27 | 1k@100MHz | FB MH3225HM601NT | 587-1755-1-ND | Inductors_SMD:L_1210
L28 | 1k@100MHz | FB MH3225HM601NT | 587-1755-1-ND | Inductors_SMD:L_1210
L29 | 1k@100MHz | FB MH3225HM601NT | 587-1755-1-ND | Inductors_SMD:L_1210
L30 | 1k@100MHz | FB MH3225HM601NT | 587-1755-1-ND | Inductors_SMD:L_1210
L31 | 1k@100MHz | FB MH3225HM601NT | 587-1755-1-ND | Inductors_SMD:L_1210
L32 | 1k@100MHz | FB MH3225HM601NT | 587-1755-1-ND | Inductors_SMD:L_1210
L33 | 1k@100MHz | FB MH3225HM601NT | 587-1755-1-ND | Inductors_SMD:L_1210
L34 | 1k@100MHz | FB MH3225HM601NT | 587-1755-1-ND | Inductors_SMD:L_1210
L35 | 1k@100MHz | FB MH3225HM601NT | 587-1755-1-ND | Inductors_SMD:L_1210
L36 | 1k@100MHz | FB MH3225HM601NT | 587-1755-1-ND | Inductors_SMD:L_1210
L37 | 1k@100MHz | FB MH3225HM601NT | 587-1755-1-ND | Inductors_SMD:L_1210
L38 | 1k@100MHz | FB MH3225HM601NT | 587-1755-1-ND | Inductors_SMD:L_1210
L39 | 1k@100MHz | FB MH3225HM601NT | 587-1755-1-ND | Inductors_SMD:L_1210
L40 | 1k@100MHz | FB MH3225HM601NT | 587-1755-1-ND | Inductors_SMD:L_1210
L41 | 1k@100MHz | FB MH3225HM601NT | 587-1755-1-ND | Inductors_SMD:L_1210
L42 | 1k@100MHz | FB MH3225HM601NT | 587-1755-1-ND | Inductors_SMD:L_1210
L43 | 1k@100MHz | FB MH3225HM601NT | 587-1755-1-ND | Inductors_SMD:L_1210
L44 | 1k@100MHz | FB MH3225HM601NT | 587-1755-1-ND | Inductors_SMD:L_1210
L45 | 1k@100MHz | FB MH3225HM601NT | 587-1755-1-ND | Inductors_SMD:L_1210

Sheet: Diodes
Ref | Value | MPN | DK | Footprint
D1 | D_TVS | SMCJ48A | SMCJ48AFSCT-ND | Diodes_SMD:DO-214AB
D2 | D | Any. Vbr > 50V |  | Diodes_THT:D_DO-41_SOD81_P10.16mm_Horizontal
D3 | D | 1SS387,L3F | 1SS387L3FCT-ND | Diodes_SMD:SOD-523
D4 | D | 1SS387,L3F | 1SS387L3FCT-ND | Diodes_SMD:SOD-523
D5 | D_Schottky | LL101C-GS08 | LL101C-GS08CT-ND | Diodes_SMD:D_MiniMELF
D6 | D_Schottky | LL101C-GS08 | LL101C-GS08CT-ND | Diodes_SMD:D_MiniMELF
D7 | D | 1SS387,L3F | 1SS387L3FCT-ND | Diodes_SMD:SOD-523
D8 | D | 1SS387,L3F | 1SS387L3FCT-ND | Diodes_SMD:SOD-523
D9 | D_Schottky | LL101C-GS08 | LL101C-GS08CT-ND | Diodes_SMD:D_MiniMELF
D10 | D_Schottky | LL101C-GS08 | LL101C-GS08CT-ND | Diodes_SMD:D_MiniMELF
D11 | D | 1SS387,L3F | 1SS387L3FCT-ND | Diodes_SMD:SOD-523
D12 | D | 1SS387,L3F | 1SS387L3FCT-ND | Diodes_SMD:SOD-523
D13 | D_Schottky | LL101C-GS08 | LL101C-GS08CT-ND | Diodes_SMD:D_MiniMELF
D14 | D_Schottky | LL101C-GS08 | LL101C-GS08CT-ND | Diodes_SMD:D_MiniMELF
D15 | D | 1SS387,L3F | 1SS387L3FCT-ND | Diodes_SMD:SOD-523
D16 | D | 1SS387,L3F | 1SS387L3FCT-ND | Diodes_SMD:SOD-523
D17 | D_Schottky | LL101C-GS08 | LL101C-GS08CT-ND | Diodes_SMD:D_MiniMELF
D18 | D_Schottky | LL101C-GS08 | LL101C-GS08CT-ND | Diodes_SMD:D_MiniMELF
D19 | LED | HLMP-1503-C0002 | 516-3190-1-ND | LEDs:LED_D3.0mm
D20 | LED | HLMP-1503-C0002 | 516-3190-1-ND | LEDs:LED_D3.0mm
D21 | LED | HLMP-1503-C0002 | 516-3190-1-ND | LEDs:LED_D3.0mm
D22 | D | S3M | S3MFSCT-ND | Diodes_SMD:DO-214AB_Handsoldering
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

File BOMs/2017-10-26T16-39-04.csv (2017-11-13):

Index | Quantity | Part Number | Description | Customer Reference | Available Quantity | Backorder Quantity | Unit Price USD | Extended Price USD
1 | 10 | CP-102B-ND | CONN PWR JACK 2.5X5.5MM SOLDER |  | 10 | 0 | 0.60000 | 6.00
2 | 10 | 151-1119-ND | CONN MOD JACK 8P8C R/A SHIELDED |  | 10 | 0 | 1.88700 | 18.87
3 | 25 | A19450-ND | CONN HEADER RTANG 2POS .100 TIN |  | 25 | 0 | 0.08400 | 2.10
4 | 69 | 296-19310-1-ND | IC OPAMP BUFFER 1GHZ SOT23-5 |  | 69 | 0 | 2.57900 | 177.95
5 | 500 | 490-4311-1-ND | CAP CER 2200PF 50V X7R 0306 |  | 500 | 0 | 0.09746 | 48.73
6 | 500 | 490-14600-1-ND | CAP CER 2.2UF 16V X5R 0402 |  | 500 | 0 | 0.04604 | 23.02
7 | 46 | 296-15172-1-ND | IC OPAMP VFB 3.9GHZ SOT23-6 |  | 46 | 0 | 5.72900 | 263.53
8 | 500 | 399-9057-1-ND | CAP CER 30PF 50V C0G/NP0 0603 |  | 500 | 0 | 0.04604 | 23.02
9 | 100 | 478-10205-1-ND | CAP CER 43PF 100V NP0 0603 |  | 100 | 0 | 0.22770 | 22.77
10 | 25 | 478-6720-1-ND | CAP CER 2.3PF 50V C0G/NP0 0603 |  | 25 | 0 | 0.44100 | 11.03
11 | 500 | 399-1061-1-ND | CAP CER 100PF 50V C0G/NP0 0603 |  | 500 | 0 | 0.01062 | 5.31
12 | 23 | ADCMP553BRMZ-ND | IC COMPARATOR PECL/LVPECL 8MSOP |  | 23 | 0 | 4.87000 | 112.01
13 | 23 | MC100ELT21DGOS-ND | IC XLATOR TTL-PECL DIFF 8SOIC |  | 23 | 0 | 3.57000 | 82.11
14 | 23 | 296-22859-1-ND | IC SWITCH DUAL SPDT 10MSOP |  | 23 | 0 | 0.78700 | 18.10
15 | 100 | 296-11933-1-ND | IC BUFFER SCHMIT TRIG SOT23-5 |  | 100 | 0 | 0.19570 | 19.57
16 | 100 | MCP6001T-I/OTCT-ND | IC OPAMP GP 1MHZ RRO SOT23-5 |  | 100 | 0 | 0.18900 | 18.90
17 | 100 | LL101C-GS08CT-ND | DIODE SCHOTTKY 40V 30MA SOD80 |  | 100 | 0 | 0.17570 | 17.57
18 | 25 | MAX9378EUA+-ND | IC TRANSLATOR SGL 8-UMAX |  | 25 | 0 | 9.35000 | 233.75
19 | 52 | 3266W-103LF-ND | TRIMMER 10K OHM 0.25W PC PIN |  | 52 | 0 | 3.05500 | 158.86
20 | 100 | 1SS387L3FCT-ND | DIODE GEN PURP 80V 100MA ESC |  | 100 | 0 | 0.12870 | 12.87
21 | 25 | A26543-ND | CONN HEADER VERT .100 2POS 15AU |  | 25 | 0 | 0.79400 | 19.85
22 | 25 | ED10563-ND | CONN TERM BLOCK 2.54MM 4POS PCB |  | 25 | 0 | 0.90400 | 22.60
23 | 25 | CT2064ST-ND | SWITCH SLIDE DIP SPST 50MA 24V |  | 25 | 0 | 0.87520 | 21.88
24 | 7 | MAX4634EUB+TCT-ND | IC MULTIPLEXER 4X1 10UMAX |  | 7 | 0 | 3.59000 | 25.13
25 | 12 | 296-39196-5-ND | IC MULTIVIBRATOR DUAL 16-SOIC |  | 12 | 0 | 0.45000 | 5.40
26 | 7 | 3310H-001-103L-ND | POT 10K OHM 1/4W PLASTIC LINEAR |  | 7 | 0 | 7.35000 | 51.45
27 | 18 | 399-9371-1-ND | CAP CER 620PF 50V C0G/NP0 1206 |  | 18 | 0 | 0.81700 | 14.71
28 | 18 | A26545-ND | CONN HEADER VERT .100 3POS 15AU |  | 18 | 0 | 0.92600 | 16.67
29 | 10 | DS90LV019TM/NOPB-ND | IC DRIVER/RECEIVER LVDS 14-SOIC |  | 10 | 0 | 2.54900 | 25.49
30 | 12 | 732-7146-ND | FIXED IND 3UH 7.6A 8.5 MOHM TH |  | 12 | 0 | 1.87000 | 22.44
31 | 7 | 1470-1968-5-ND | DC/DC CONVERTER +/-5V 10W |  | 7 | 0 | 24.73600 | 173.15
32 | 7 | 102-2833-ND | DC/DC CONVERTER 15V 200MA 3W |  | 7 | 0 | 13.36200 | 93.53
33 | 100 | 587-2988-1-ND | CAP CER 4.7UF 50V X5R 1206 |  | 100 | 0 | 0.12040 | 12.04
34 | 10 | AIUR-07-120K-ND | FIXED IND 12UH 980MA 120 MOHM TH |  | 10 | 0 | 0.70000 | 7.00
35 | 7 | M8872-ND | FIXED IND 56UH 6.4A 26 MOHM TH |  | 7 | 0 | 3.42000 | 23.94
36 | 100 | P5184-ND | CAP ALUM 330UF 20% 50V RADIAL |  | 100 | 0 | 0.20920 | 20.92
37 | 10 | SMCJ48AFSCT-ND | TVS DIODE 48VWM 77.4VC SMC |  | 10 | 0 | 0.47800 | 4.78
38 | 100 | 493-13464-1-ND | CAP ALUM 100UF 20% 50V RADIAL |  | 100 | 0 | 0.13690 | 13.69
39 | 100 | RLB0914-120KL-ND | FIXED IND 12UH 2.5A 55 MOHM TH |  | 100 | 0 | 0.21250 | 21.25
40 | 100 | P19712CT-ND | CAP ALUM 100UF 20% 50V RADIAL |  | 100 | 0 | 0.20760 | 20.76
41 | 12 | 311-0.18LWCT-ND | RES 0.18 OHM 1% 1/4W 1206 |  | 12 | 0 | 0.33000 | 3.96
42 | 10 | F1504-ND | FUSE BLOK CARTRIDGE 600V 10A PCB |  | 10 | 0 | 1.13700 | 11.37
43 | 10 | 311-.4QCT-ND | RES 0.4 OHM 1% 1/10W 0603 |  | 10 | 0 | 0.27200 | 2.72
44 | 7 | 360-3351-ND | SWITCH PUSH SPDT 0.4VA 28V |  | 7 | 0 | 4.70000 | 32.90
45 | 100 | C503B-GCN-CY0C0791-ND | LED GREEN CLEAR 5MM ROUND T/H |  | 100 | 0 | 0.20980 | 20.98
46 | 100 | 36-5001-ND | TEST POINT PC MINI .040"D BLACK |  | 100 | 0 | 0.22090 | 22.09
47 | 25 | 36-1902E-ND | HEX STANDOFF 4-40 NYLON 1" |  | 25 | 0 | 0.69700 | 17.43
48 | 25 | 36-4808-ND | HEX STANDOFF 4-40 NYLON 1-1/4" |  | 25 | 0 | 0.49400 | 12.35
49 | 50 | 732-10381-ND | HEX STANDOFF M3 STEEL 5MM |  | 50 | 0 | 0.26400 | 13.20
50 | 50 | 36-7689-1-ND | MACHINE SCREW COMBINATION M3 |  | 50 | 0 | 0.17560 | 8.78
51 | 5 | HM1506-ND | BOX ALUM BLUE 8.66"L X 6.5"W |  | 5 | 0 | 31.32800 | 156.64
52 | 100 | 311-39.0HRCT-ND | RES SMD 39 OHM 1% 1/10W 0603 |  | 100 | 0 | 0.00600 | 0.60
53 | 500 | 399-4925-1-ND | CAP CER 10UF 10V X5R 0805 |  | 500 | 0 | 0.03086 | 15.43
54 | 25 | 445-6007-1-ND | CAP CER 100UF 10V X5R 1206 |  | 25 | 0 | 1.25200 | 31.30
55 | 250 | 587-1755-1-ND | FERRITE BEAD 600 OHM 1210 1LN |  | 250 | 0 | 0.14256 | 35.64
56 | 100 | YAG3125DKR-ND | RES SMD 34.8K OHM 1% 1/16W 0402 |  | 100 | 0 | 0.07550 | 7.55
57 | 100 | 311-82.5HRCT-ND | RES SMD 82.5 OHM 1% 1/10W 0603 |  | 100 | 0 | 0.00600 | 0.60
58 | 100 | 311-124HRCT-ND | RES SMD 124 OHM 1% 1/10W 0603 |  | 100 | 0 | 0.00600 | 0.60
59 | 100 | S9000-ND | CONN JUMPER SHORTING TIN |  | 100 | 0 | 0.03650 | 3.65
60 | 100 | 311-10KGRCT-ND | RES SMD 10K OHM 5% 1/10W 0603 |  | 100 | 0 | 0.00460 | 0.46
61 | 100 | 709-1036-6-ND | CAP CER 1000PF 2KV X7R 1206 |  | 100 | 0 | 0.11680 | 11.68
62 | 100 | 493-11380-1-ND | CAP ALUM 12UF 20% 35V RADIAL |  | 100 | 0 | 0.10840 | 10.84
63 | 100 | 36-4708-ND | HEX NUT 0.217" STEEL M3 |  | 100 | 0 | 0.08440 | 8.44
64 | 100 | 311-470HRCT-ND | RES SMD 470 OHM 1% 1/10W 0603 |  | 100 | 0 | 0.00600 | 0.60
65 | 161 | 490-4392-1-ND | CAP CER 4.7UF 6.3V X7R 0612 |  | 161 | 0 | 0.34490 | 55.53
66 | 25 | 399-1061-6-ND | CAP CER 100PF 50V C0G/NP0 0603 |  | 25 | 0 | 0.31320 | 7.83
67 | 10 | CSR2010JTR300CT-ND | RES 0.3 OHM 5% 1W 2010 |  | 10 | 0 | 0.38000 | 3.80
68 | 25 | 3266W-503LF-ND | TRIMMER 50K OHM 0.25W PC PIN |  | 25 | 0 | 3.25000 | 81.25

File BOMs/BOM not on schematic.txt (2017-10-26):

36-1902E-ND	4
36-4808-ND	4
732-10381-ND	3
36-4708-NDf	3
36-7689-1-ND	3
HM1506-ND	1

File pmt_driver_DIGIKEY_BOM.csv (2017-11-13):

Digikey item | Count
1124-1356-ND | 5
1124-1421-ND | 12
CP-102B-ND | 1
151-1119-ND | 1
A19450-ND | 1
296-19310-1-ND | 12
490-4311-1-ND | 84
587-1755-1-ND | 40
490-10695-1-ND | 48
311-39.0HRTR-ND | 16
296-15172-1-ND | 8
311-470HRCT-ND | 4
399-9057-1-ND | 4
YAG3125CT-ND | 4
478-10205-1-ND | 4
478-6720-1-ND | 4
399-1061-1-ND | 8
ADCMP553BRMZ-ND | 4
MC100ELT21DGOS-ND | 4
296-22859-1-ND | 4
296-11933-1-ND | 4
MCP6001T-I/OTCT-ND | 4
311-82.5HRCT-ND | 8
311-124HRCT-ND | 8
3266W-503LF-ND | 4
LL101C-GS08CT-ND | 8
MAX9378EUA+-ND | 4
490-4392-1-ND | 28
3266W-103LF-ND | 11
1SS387L3FCT-ND | 8
36-11011-R-ND | 6
S9000-ND | 7
A26543-ND | 4
ED10563-ND | 4
CT2064ST-ND | 3
311-10KGRCT-ND | 12
MAX4634EUB+TCT-ND | 1
296-39196-5-ND | 2
399-9371-1-ND | 3
A26545-ND | 3
DS90LV019TM/NOPB-ND | 1
399-4925-2-ND | 4
732-7146-ND | 2
1470-1968-5-ND | 1
102-2833-ND | 1
709-1036-1-ND | 1
587-2988-1-ND | 2
AIUR-07-120K-ND | 1
M8872-ND | 1
P5184-ND | 2
SMCJ48AFSCT-ND | 1
493-11380-1-ND | 1
493-13464-1-ND | 2
RLB0914-120KL-ND | 1
P19712CT-ND | 4
445-6007-2-ND | 4
311-0.18LWCT-ND | 2
F1504-ND | 1
311-.4QCT-ND | 1
CSR2010JTR300CT-ND | 1
360-3351-ND | 1
C503B-GCN-CY0C0791-ND | 3
36-5001-ND | 9
S3MFSCT-ND | 1
36-11011-B-ND | 1

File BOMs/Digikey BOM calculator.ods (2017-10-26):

Digikey item | Count | Multiplied | With spares | Raised to price break | Multiplier | Spares (percent) | Price breaks | Price break limit (percent)
1124-1356-ND | 5 | 25 | 29 | 29 | 5 | 15 | 0 | 20
1124-1421-ND | 12 | 60 | 69 | 69 |  | Spares (min count) | 10
CP-102B-ND | 1 | 5 | 7 | 7 |  | 2 | 25
151-1119-ND | 1 | 5 | 7 | 7 |  |  | 50
A19450-ND | 1 | 5 | 7 | 7 |  |  | 100
296-19310-1-ND | 12 | 60 | 69 | 69 |  |  | 500
490-4311-1-ND | 84 | 420 | 483 | 500 |  |  | 1000
587-1755-1-ND | 40 | 200 | 230 | 230 |  |  | 2500
490-14600-1-ND | 44 | 220 | 253 | 253 |  |  | 5000
311-39.0HRTR-ND | 16 | 80 | 92 | 100
296-15172-1-ND | 8 | 40 | 46 | 50
311-470HRCT-ND | 4 | 20 | 23 | 25
399-9057-1-ND | 4 | 20 | 23 | 25
YAG3125DKR-ND | 4 | 20 | 23 | 25
478-10205-1-ND | 4 | 20 | 23 | 25
478-6720-1-ND | 4 | 20 | 23 | 25
399-1061-1-ND | 4 | 20 | 23 | 25
ADCMP553BRMZ-ND | 4 | 20 | 23 | 25
MC100ELT21DGOS-ND | 4 | 20 | 23 | 25
296-22859-1-ND | 4 | 20 | 23 | 25
296-11933-1-ND | 4 | 20 | 23 | 25
MCP6001T-I/OTCT-ND | 4 | 20 | 23 | 25
311-82.5HRCT-ND | 8 | 40 | 46 | 50
311-124HRCT-ND | 8 | 40 | 46 | 50
3266W-503LF-ND | 4 | 20 | 23 | 25
399-1061-6-ND | 4 | 20 | 23 | 25
LL101C-GS08CT-ND | 8 | 40 | 46 | 50
MAX9378EUA+-ND | 4 | 20 | 23 | 25
490-4392-1-ND | 28 | 140 | 161 | 161
3266W-103LF-ND | 9 | 45 | 52 | 52
1SS387L3FCT-ND | 8 | 40 | 46 | 50
S9000-ND | 7 | 35 | 41 | 41
A26543-ND | 4 | 20 | 23 | 25
ED10563-ND | 4 | 20 | 23 | 25
CT2064ST-ND | 3 | 15 | 18 | 18
311-10KGRCT-ND | 12 | 60 | 69 | 69
MAX4634EUB+TCT-ND | 1 | 5 | 7 | 7
296-39196-5-ND | 2 | 10 | 12 | 12
3310H-001-103L-ND | 1 | 5 | 7 | 7
399-9371-1-ND | 3 | 15 | 18 | 18
A26545-ND | 3 | 15 | 18 | 18
DS90LV019TM/NOPB-ND | 1 | 5 | 7 | 7
399-4925-2-ND | 4 | 20 | 23 | 25
732-7146-ND | 2 | 10 | 12 | 12
1470-1968-5-ND | 1 | 5 | 7 | 7
102-2833-ND | 1 | 5 | 7 | 7
709-1036-6-ND | 1 | 5 | 7 | 7
587-2988-1-ND | 2 | 10 | 12 | 12
AIUR-07-120K-ND | 1 | 5 | 7 | 7
M8872-ND | 1 | 5 | 7 | 7
P5184-ND | 2 | 10 | 12 | 12
SMCJ48AFSCT-ND | 1 | 5 | 7 | 7
493-11380-1-ND | 1 | 5 | 7 | 7
493-13464-1-ND | 2 | 10 | 12 | 12
RLB0914-120KL-ND | 1 | 5 | 7 | 7
P19712CT-ND | 4 | 20 | 23 | 25
445-6007-2-ND | 4 | 20 | 23 | 25
311-0.18LWCT-ND | 2 | 10 | 12 | 12
F1504-ND | 1 | 5 | 7 | 7
311-.4QCT-ND | 1 | 5 | 7 | 7
CSR2010JTR300CT-ND | 1 | 5 | 7 | 7
360-3351-ND | 1 | 5 | 7 | 7
C503B-GCN-CY0C0791-ND | 3 | 15 | 18 | 18
36-5001-ND | 10 | 50 | 58 | 58
36-1902E-ND | 4 | 20 | 23 | 25
36-4808-ND | 4 | 20 | 23 | 25
732-10381-ND | 3 | 15 | 18 | 18
36-4708-NDf | 3 | 15 | 18 | 18
36-7689-1-ND | 3 | 15 | 18 | 18
HM1506-ND | 1 | 5 | 7 | 7
 |  | 0 | 2 | 2
 |  | 0 | 2 | 2
 |  | 0 | 2 | 2
 |  | 0 | 2 | 2
 |  | 0 | 2 | 2
 |  | 0 | 2 | 2
 |  | 0 | 2 | 2
 |  | 0 | 2 | 2
 |  | 0 | 2 | 2
 |  | 0 | 2 | 2
 |  | 0 | 2 | 2
 |  | 0 | 2 | 2
 |  | 0 | 2 | 2
 |  | 0 | 2 | 2
 |  | 0 | 2 | 2
 |  | 0 | 2 | 2
 |  | 0 | 2 | 2
 |  | 0 | 2 | 2
 |  | 0 | 2 | 2
 |  | 0 | 2 | 2
 |  | 0 | 2 | 2
 |  | 0 | 2 | 2
 |  | 0 | 2 | 2
 |  | 0 | 2 | 2
 |  | 0 | 2 | 2
 |  | 0 | 2 | 2
 |  | 0 | 2 | 2
 |  | 0 | 2 | 2
 |  | 0 | 2 | 2
 |  | 0 | 2 | 2
 |  | 0 | 2 | 2
 |  | 0 | 2 | 2
 |  | 0 | 2 | 2
 |  | 0 | 2 | 2
 |  | 0 | 2 | 2
 |  | 0 | 2 | 2
 |  | 0 | 2 | 2
 |  | 0 | 2 | 2
 |  | 0 | 2 | 2
 |  | 0 | 2 | 2
 |  | 0 | 2 | 2
 |  | 0 | 2 | 2
 |  | 0 | 2 | 2
 |  | 0 | 2 | 2
 |  | 0 | 2 | 2
 |  | 0 | 2 | 2
 |  | 0 | 2 | 2
 |  | 0 | 2 | 2
 |  | 0 | 2 | 2
 |  | 0 | 2 | 2
 |  | 0 | 2 | 2
 |  | 0 | 2 | 2
 |  | 0 | 2 | 2
 |  | 0 | 2 | 2
 |  | 0 | 2 | 2
 |  | 0 | 2 | 2
 |  | 0 | 2 | 2
 |  | 0 | 2 | 2
 |  | 0 | 2 | 2
 |  | 0 | 2 | 2
 |  | 0 | 2 | 2
 |  | 0 | 2 | 2
 |  | 0 | 2 | 2
 |  | 0 | 2 | 2
 |  | 0 | 2 | 2
 |  | 0 | 2 | 2
 |  | 0 | 2 | 2
 |  | 0 | 2 | 2
 |  | 0 | 2 | 2
 |  | 0 | 2 | 2
 |  | 0 | 2 | 2
 |  | 0 | 2 | 2
 |  | 0 | 2 | 2
 |  | 0 | 2 | 2
 |  | 0 | 2 | 2
 |  | 0 | 2 | 2
 |  | 0 | 2 | 2
 |  | 0 | 2 | 2
 |  | 0 | 2 | 2
 |  | 0 | 2 | 2
 |  | 0 | 2 | 2
 |  | 0 | 2 | 2
 |  | 0 | 2 | 2
 |  | 0 | 2 | 2
 |  | 0 | 2 | 2
 |  | 0 | 2 | 2
 |  | 0 | 2 | 2
 |  | 0 | 2 | 2
 |  | 0 | 2 | 2
 |  | 0 | 2 | 2
 |  | 0 | 2 | 2
 |  | 0 | 2 | 2
 |  | 0 | 2 | 2
 |  | 0 | 2 | 2
 |  | 0 | 2 | 2
 |  | 0 | 2 | 2
 |  | 0 | 2 | 2
 |  | 0 | 2 | 2
 |  | 0 | 2 | 2
 |  | 0 | 2 | 2
 |  | 0 | 2 | 2
 |  | 0 | 2 | 2
 |  | 0 | 2 | 2
 |  | 0 | 2 | 2
 |  | 0 | 2 | 2
 |  | 0 | 2 | 2
 |  | 0 | 2 | 2
 |  | 0 | 2 | 2
 |  | 0 | 2 | 2
 |  | 0 | 2 | 2
 |  | 0 | 2 | 2
 |  | 0 | 2 | 2
 |  | 0 | 2 | 2
 |  | 0 | 2 | 2
 |  | 0 | 2 | 2
 |  | 0 | 2 | 2
 |  | 0 | 2 | 2
 |  | 0 | 2 | 2
 |  | 0 | 2 | 2
 |  | 0 | 2 | 2
 |  | 0 | 2 | 2
 |  | 0 | 2 | 2
 |  | 0 | 2 | 2
 |  | 0 | 2 | 2
 |  | 0 | 2 | 2
 |  | 0 | 2 | 2
 |  | 0 | 2 | 2
 |  | 0 | 2 | 2
 |  | 0 | 2 | 2
 |  | 0 | 2 | 2
 |  | 0 | 2 | 2
 |  | 0 | 2 | 2
 |  | 0 | 2

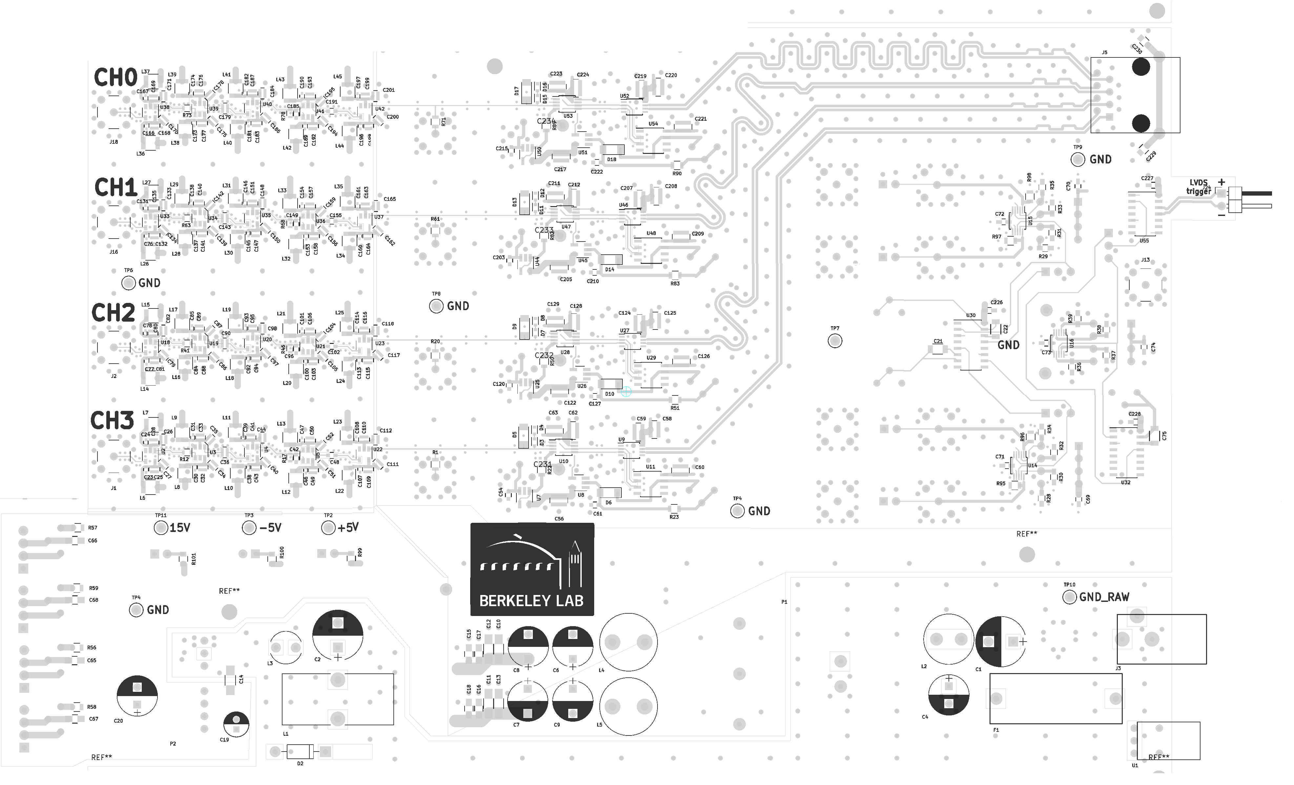
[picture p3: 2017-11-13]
Schematics and drawings/Components Back.png

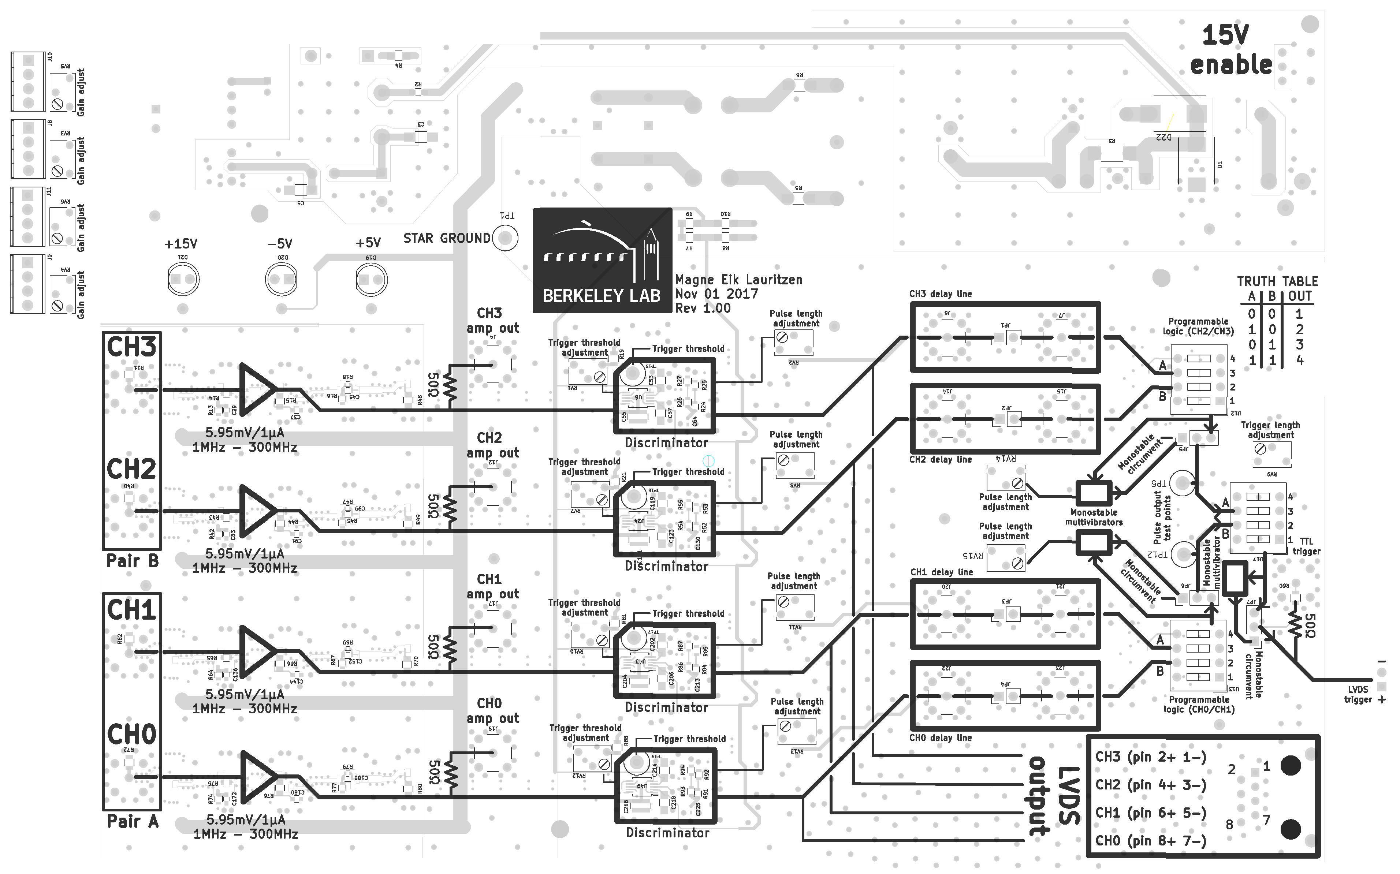
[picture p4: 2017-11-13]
Schematics and drawings/Components Front.png

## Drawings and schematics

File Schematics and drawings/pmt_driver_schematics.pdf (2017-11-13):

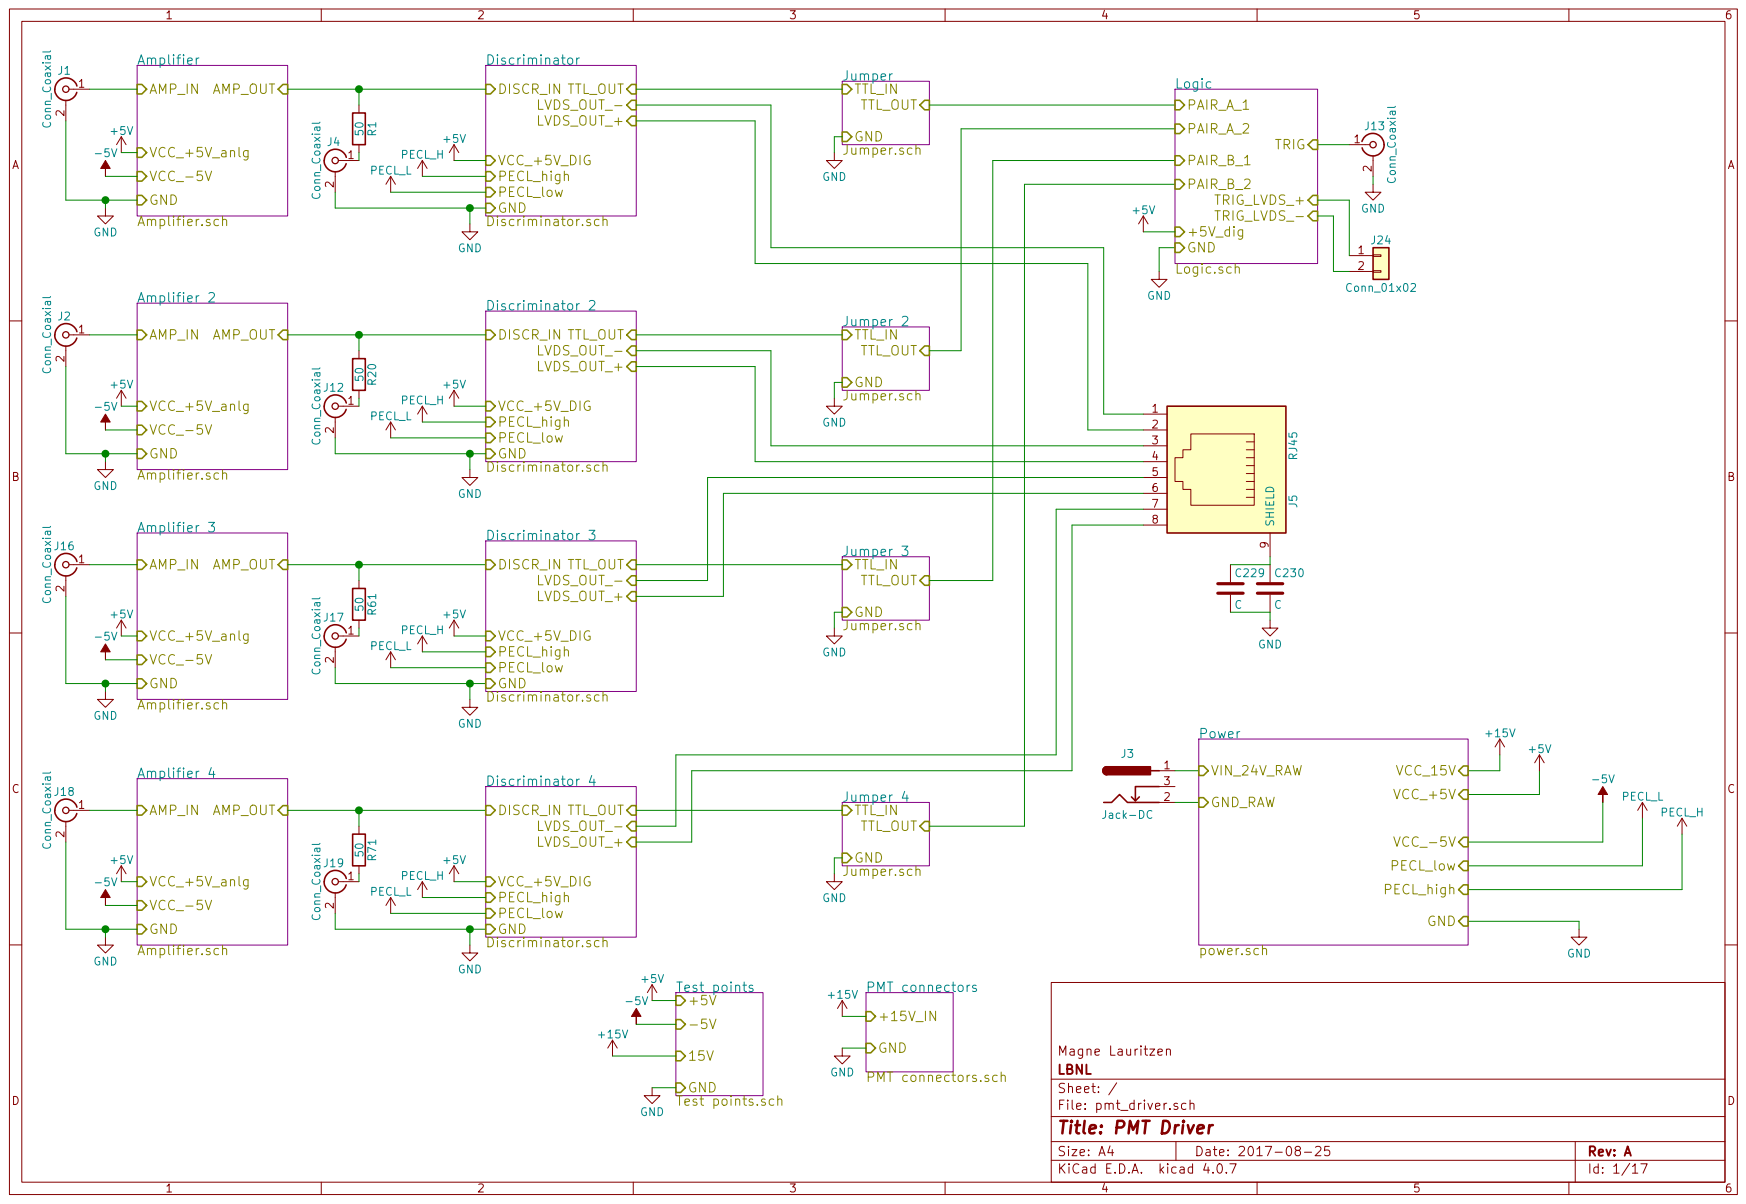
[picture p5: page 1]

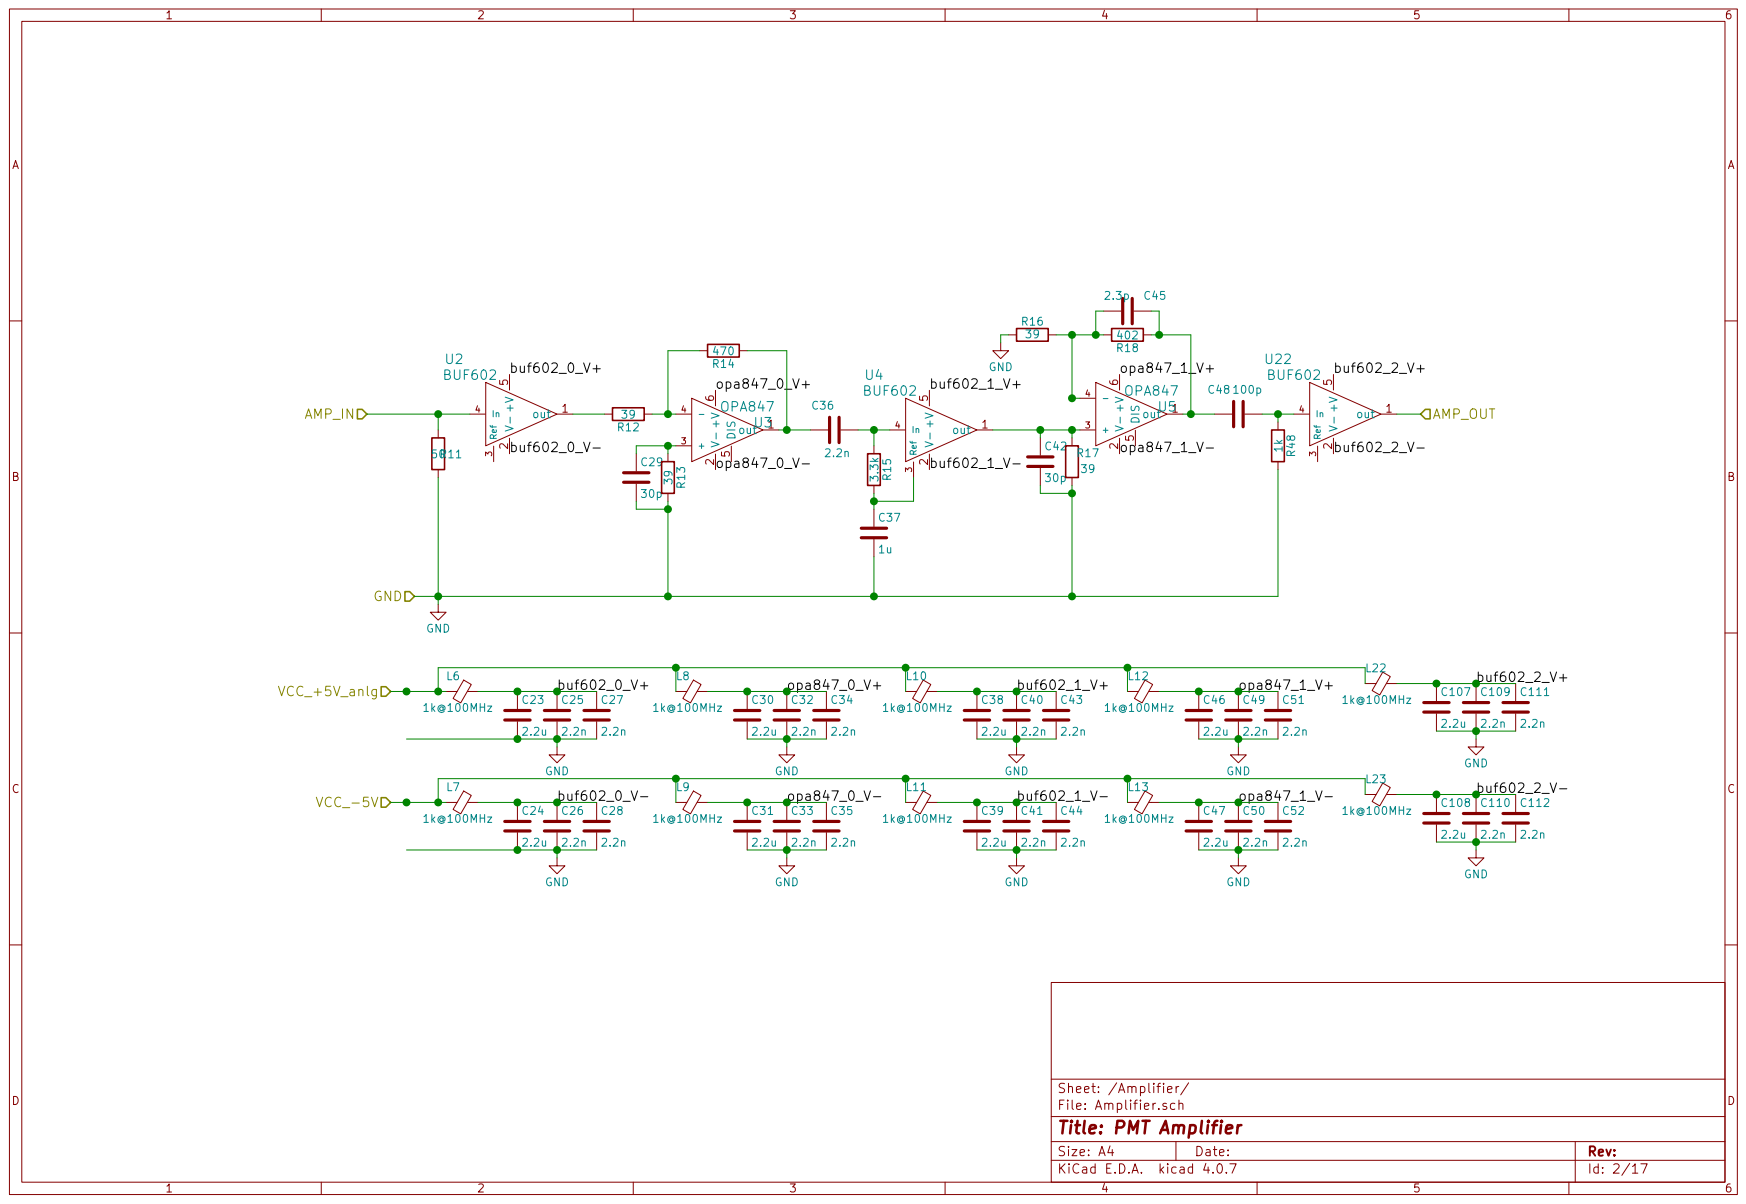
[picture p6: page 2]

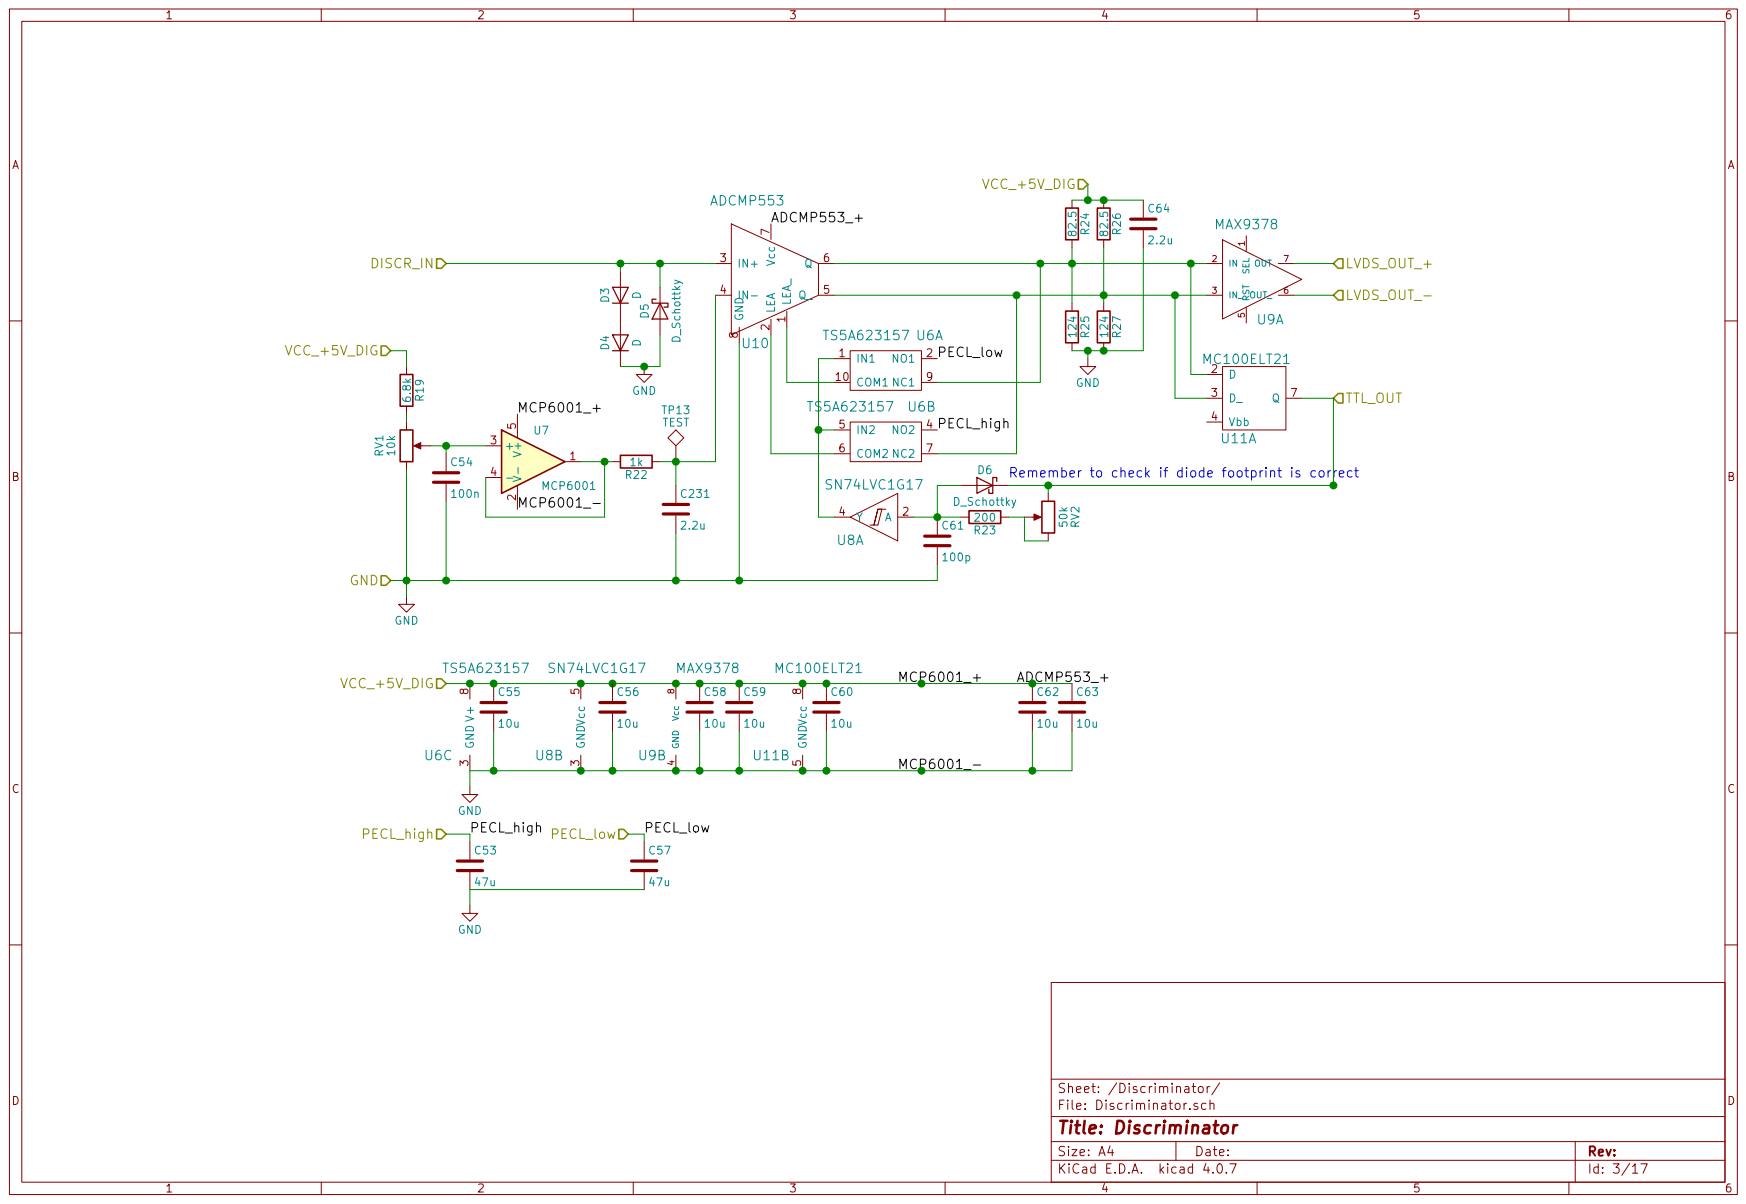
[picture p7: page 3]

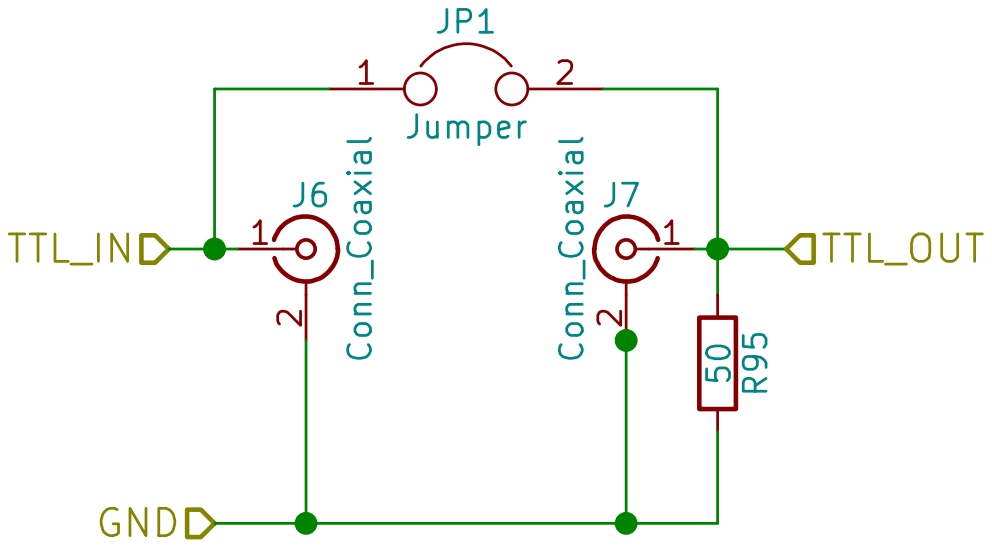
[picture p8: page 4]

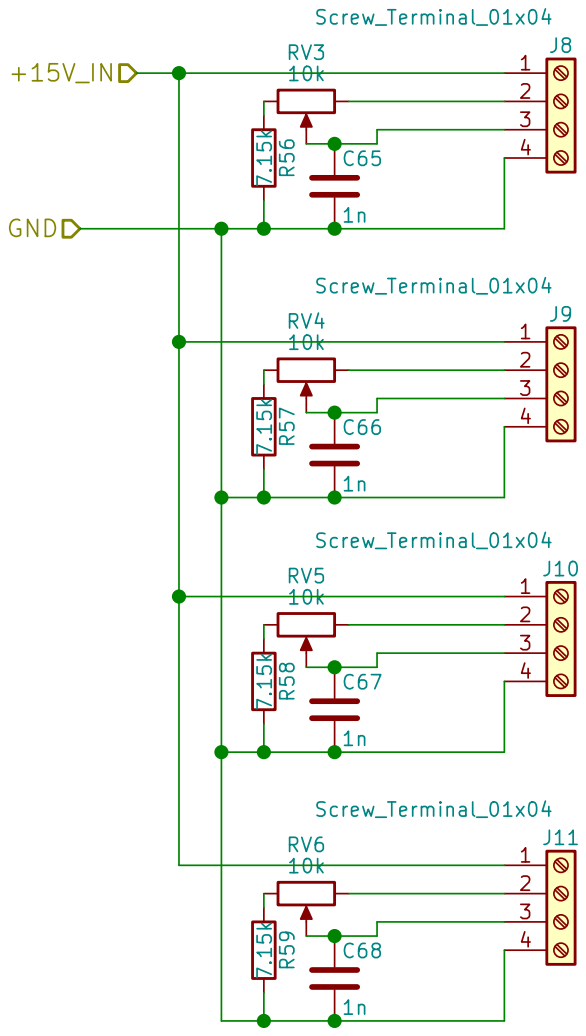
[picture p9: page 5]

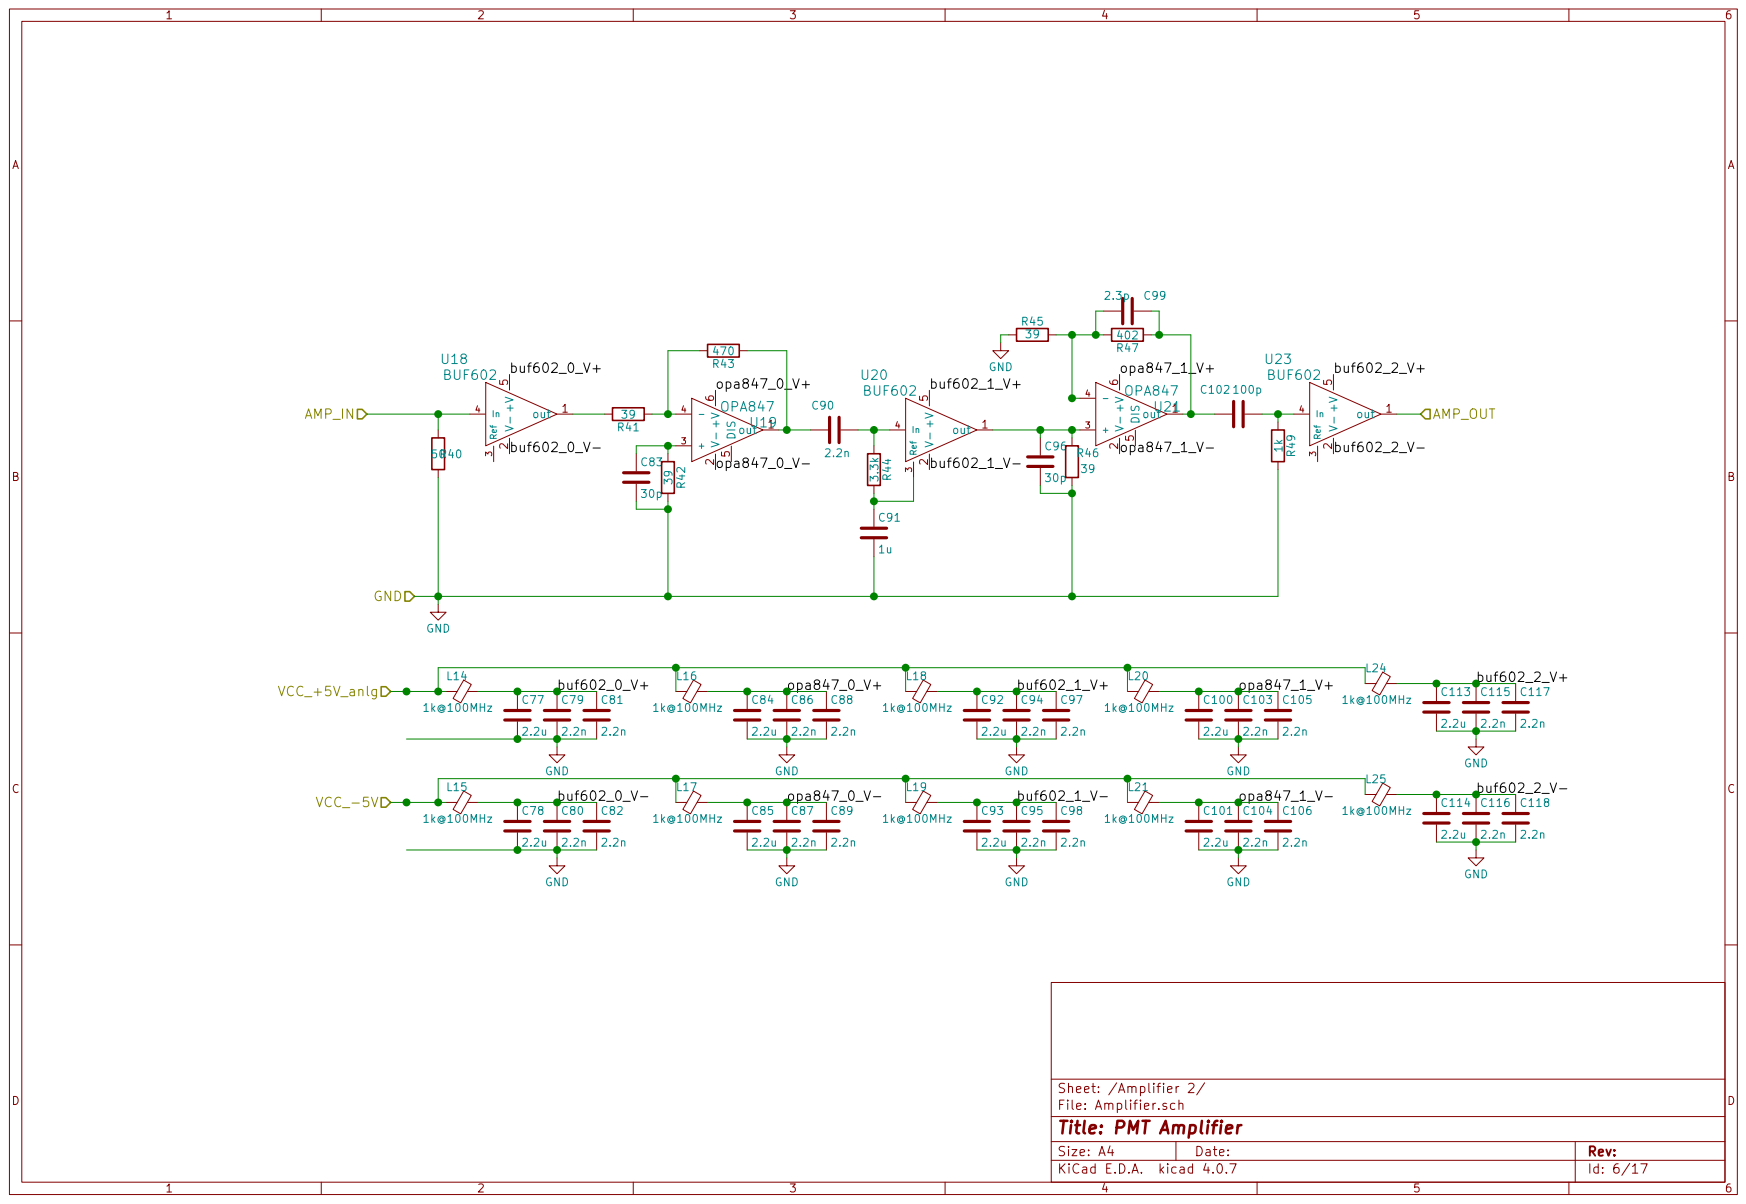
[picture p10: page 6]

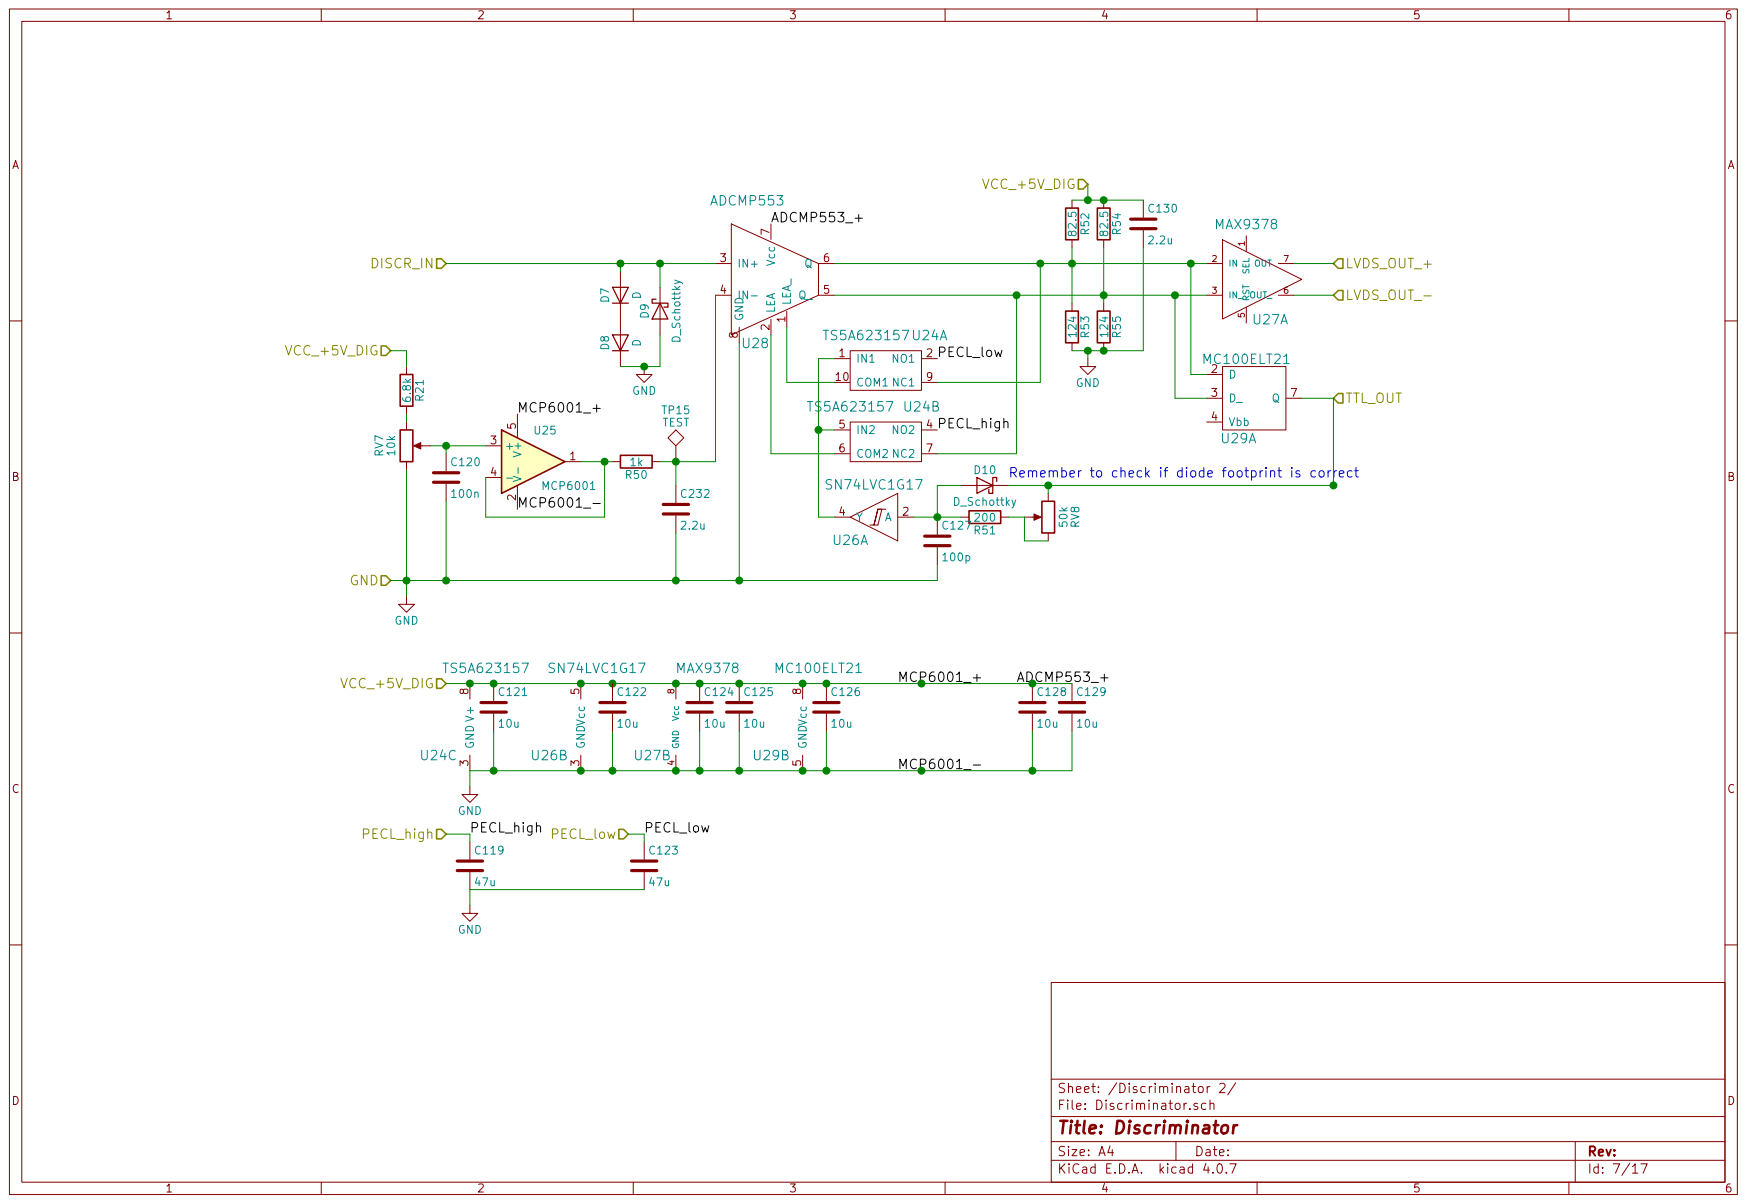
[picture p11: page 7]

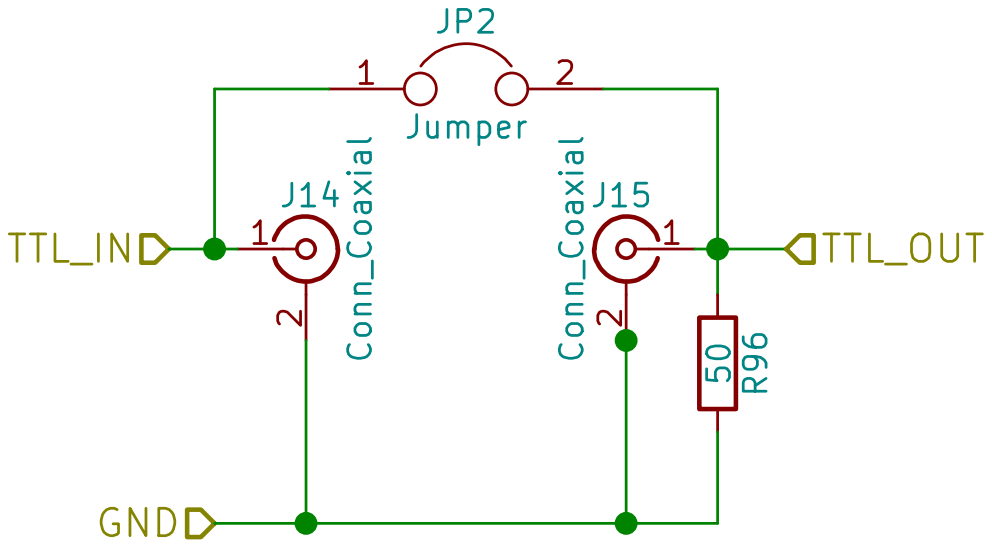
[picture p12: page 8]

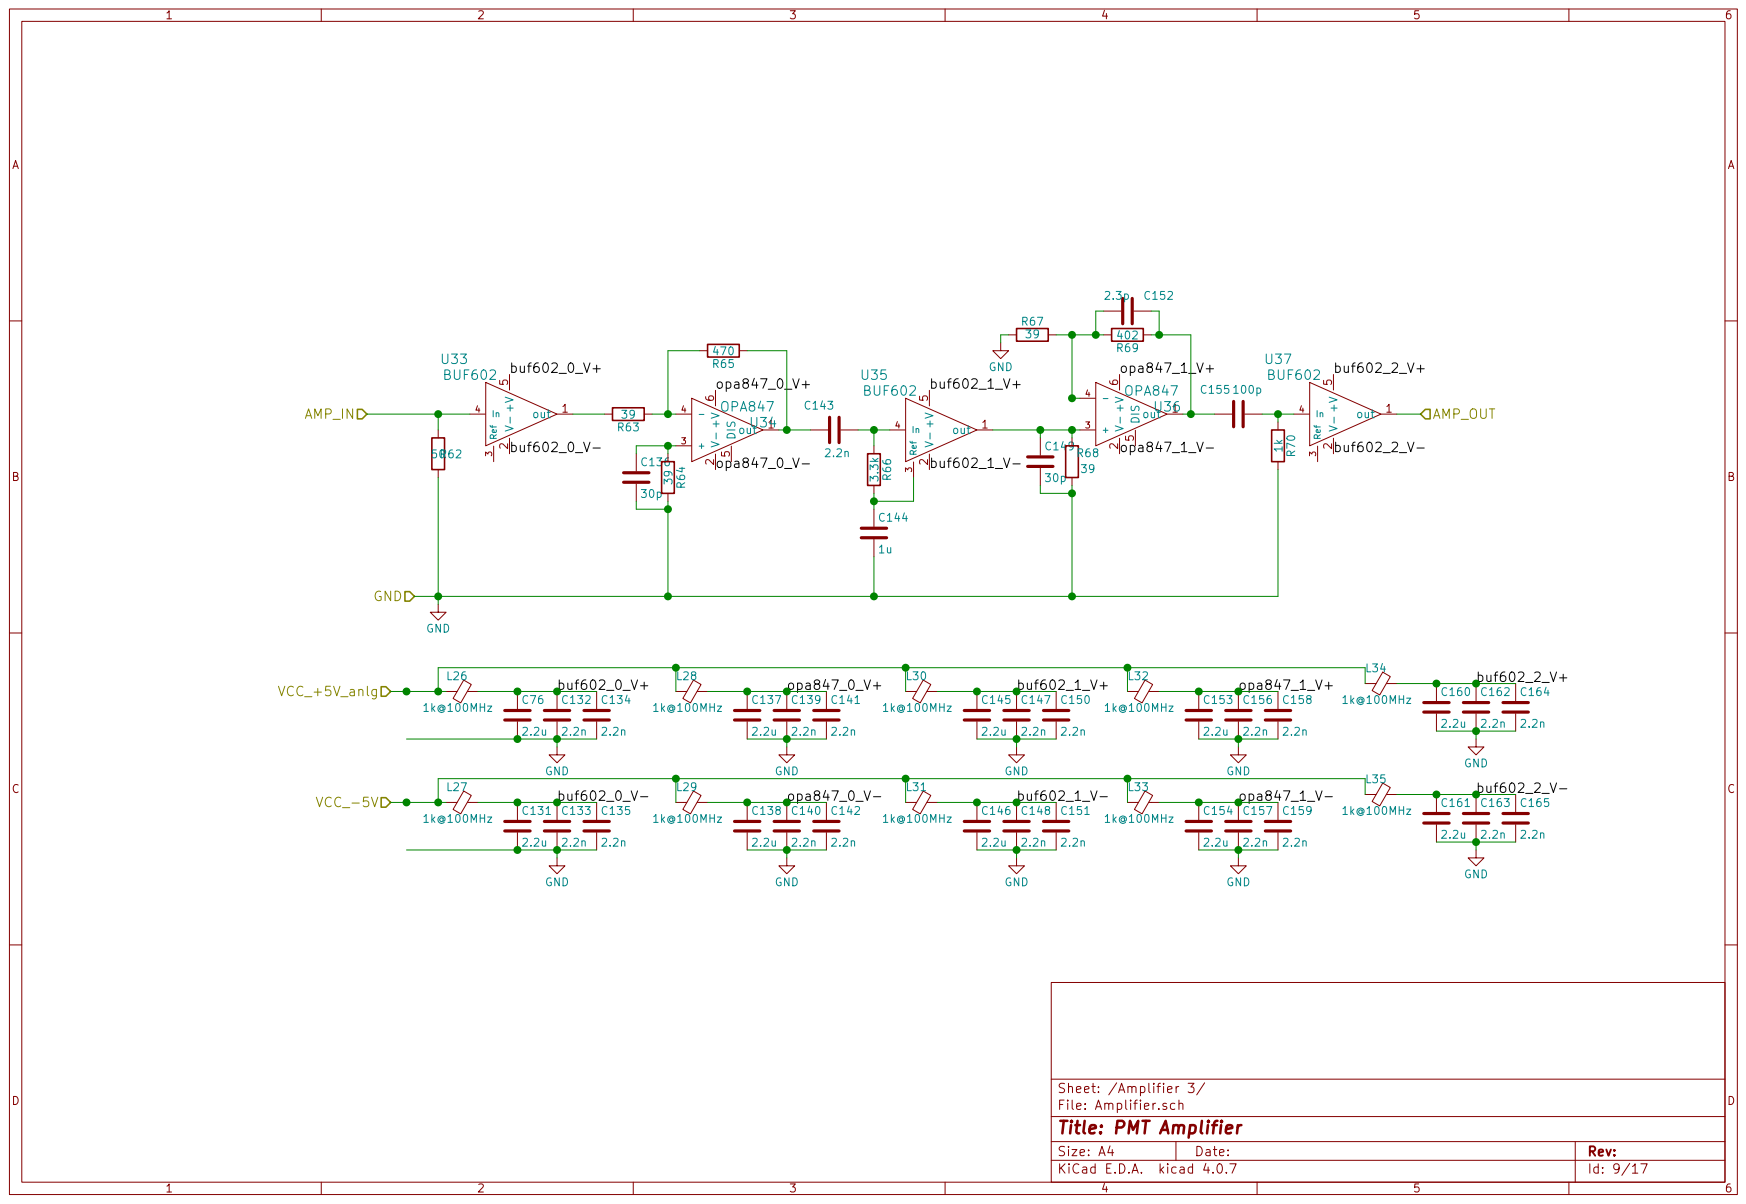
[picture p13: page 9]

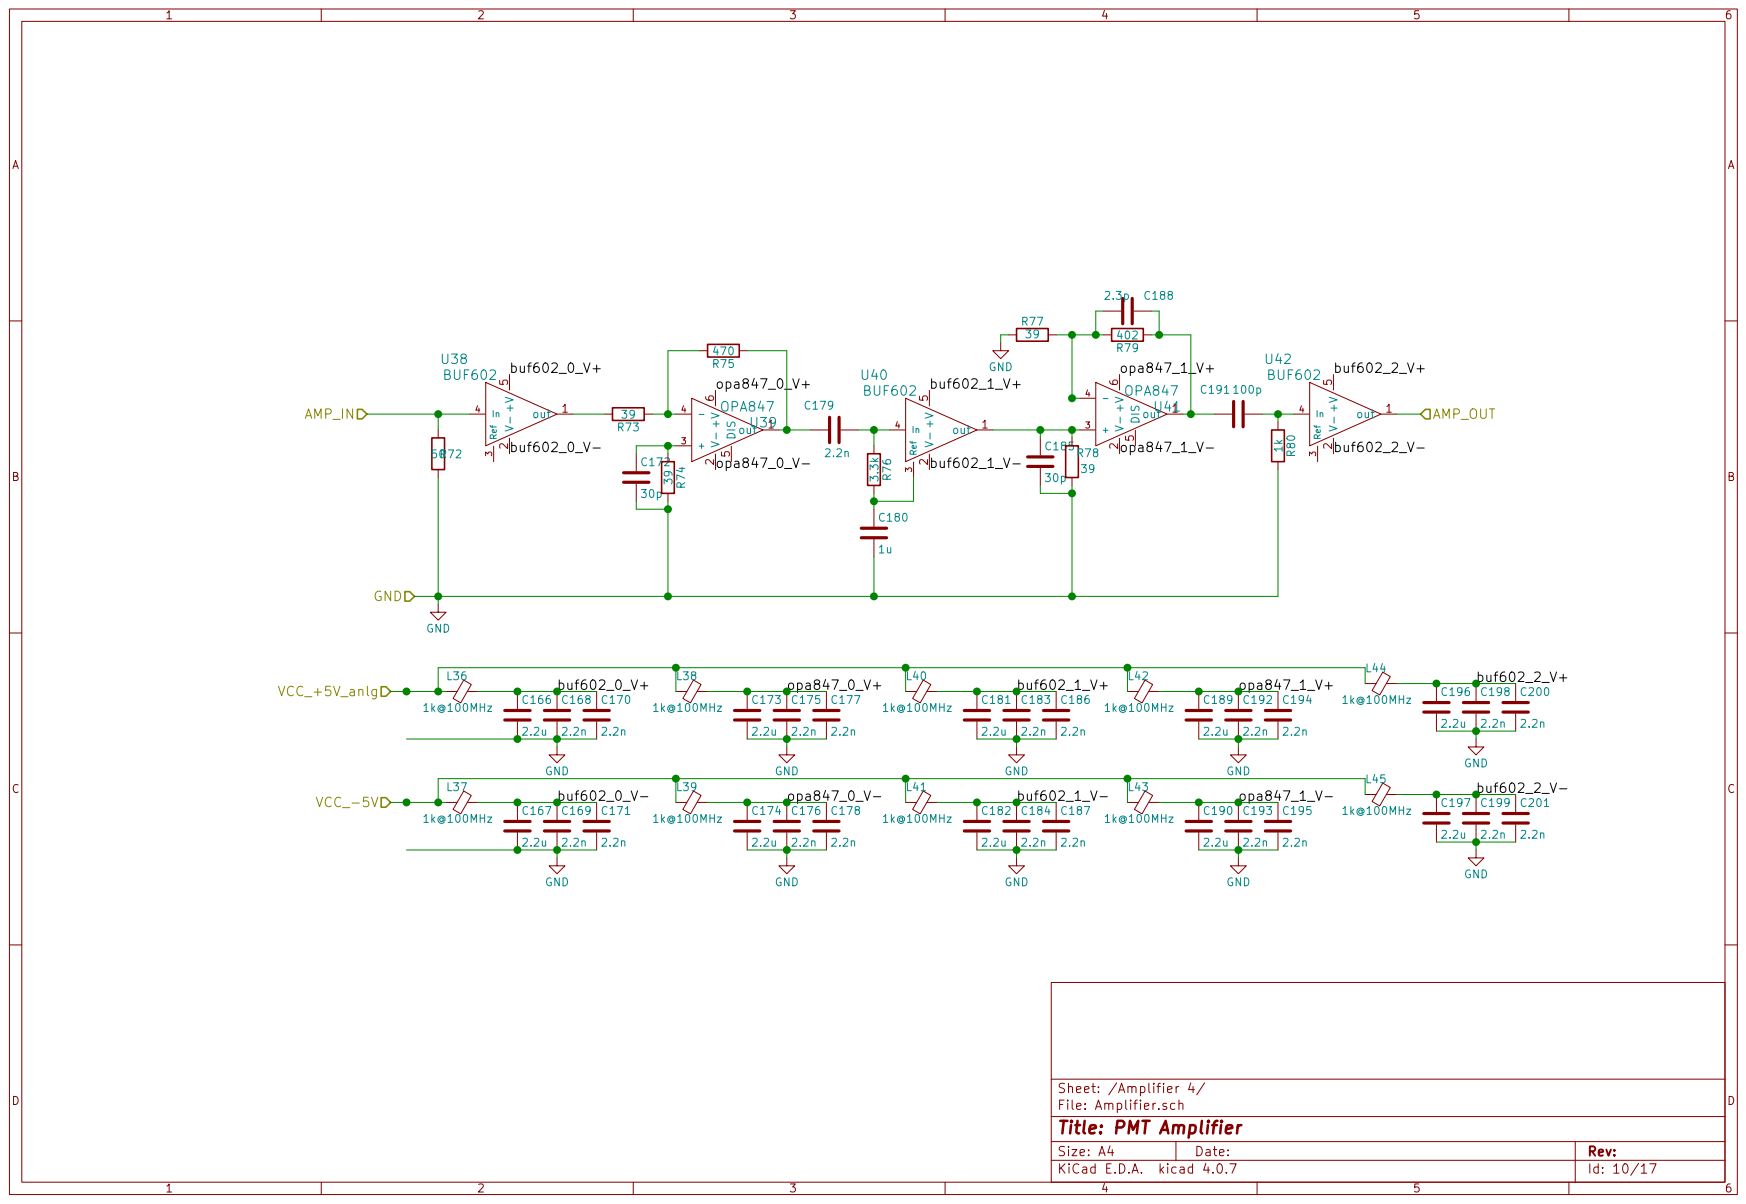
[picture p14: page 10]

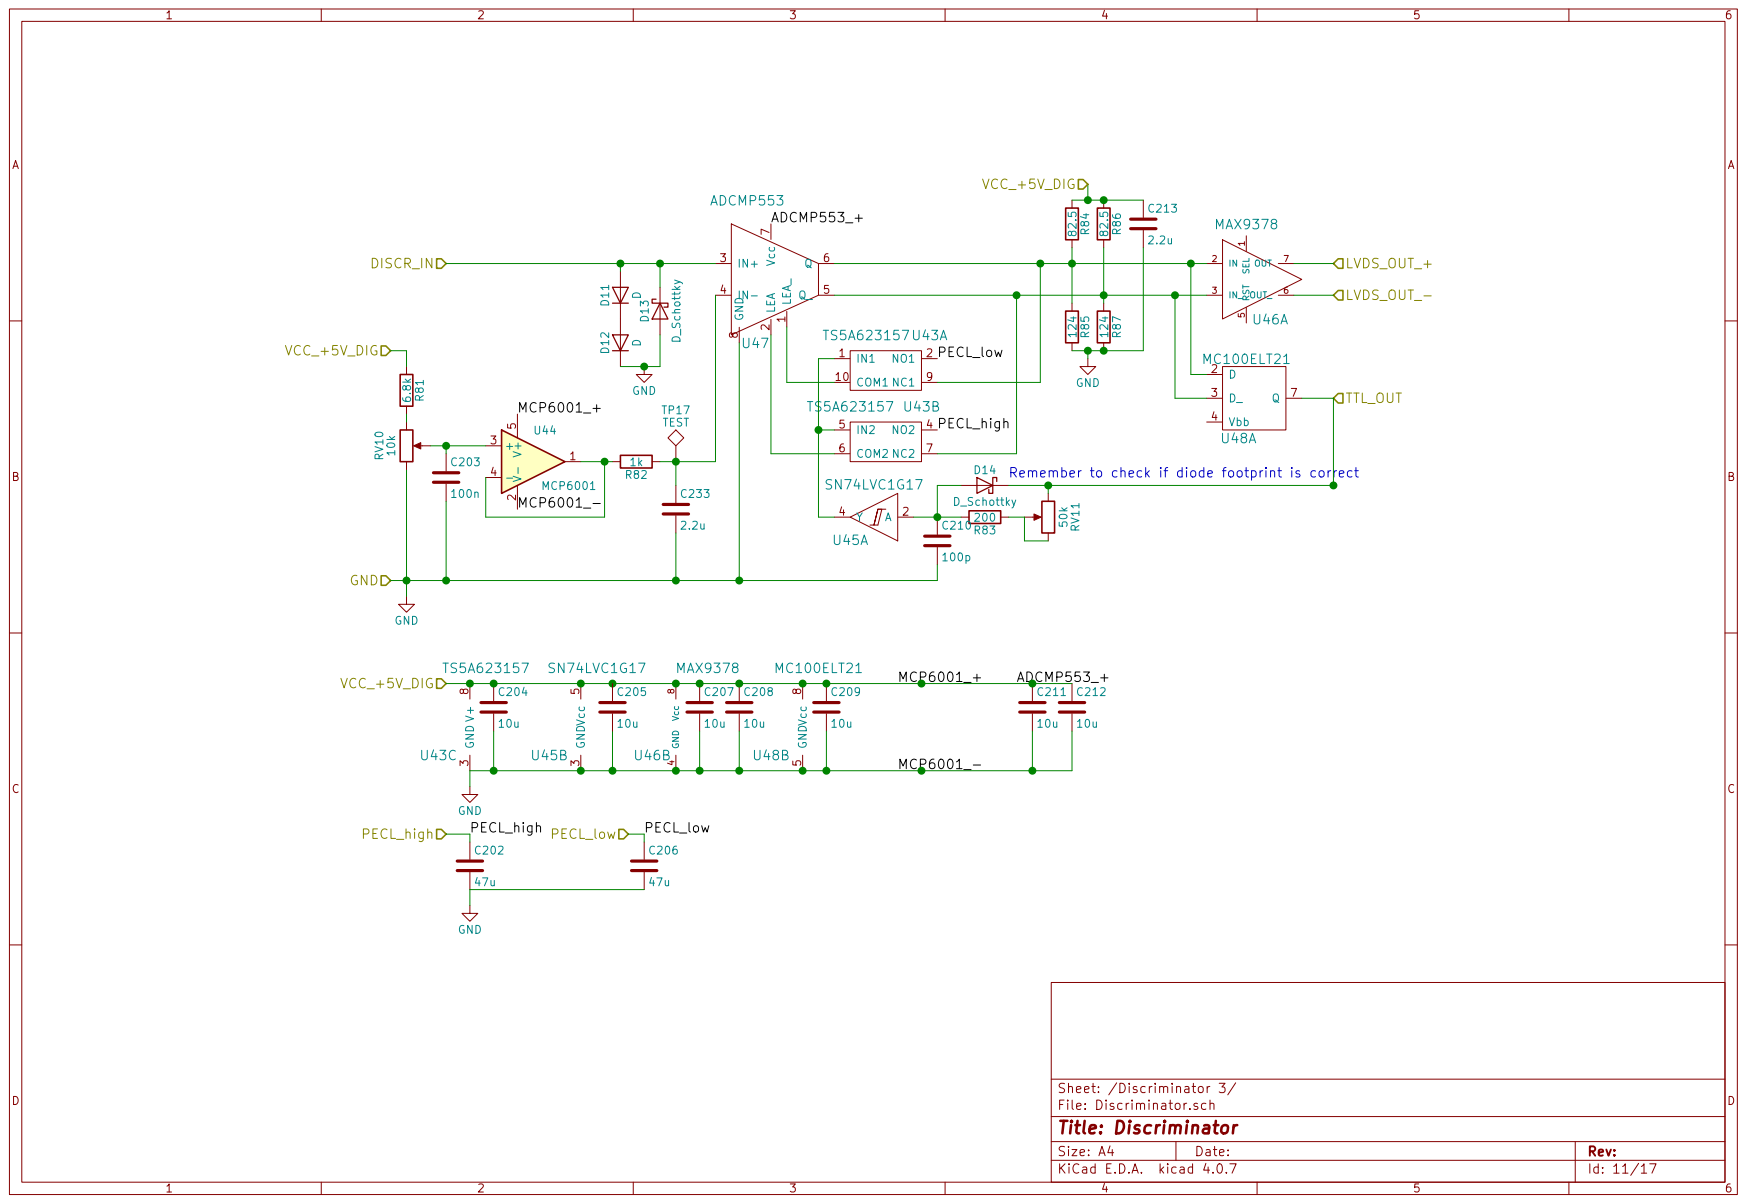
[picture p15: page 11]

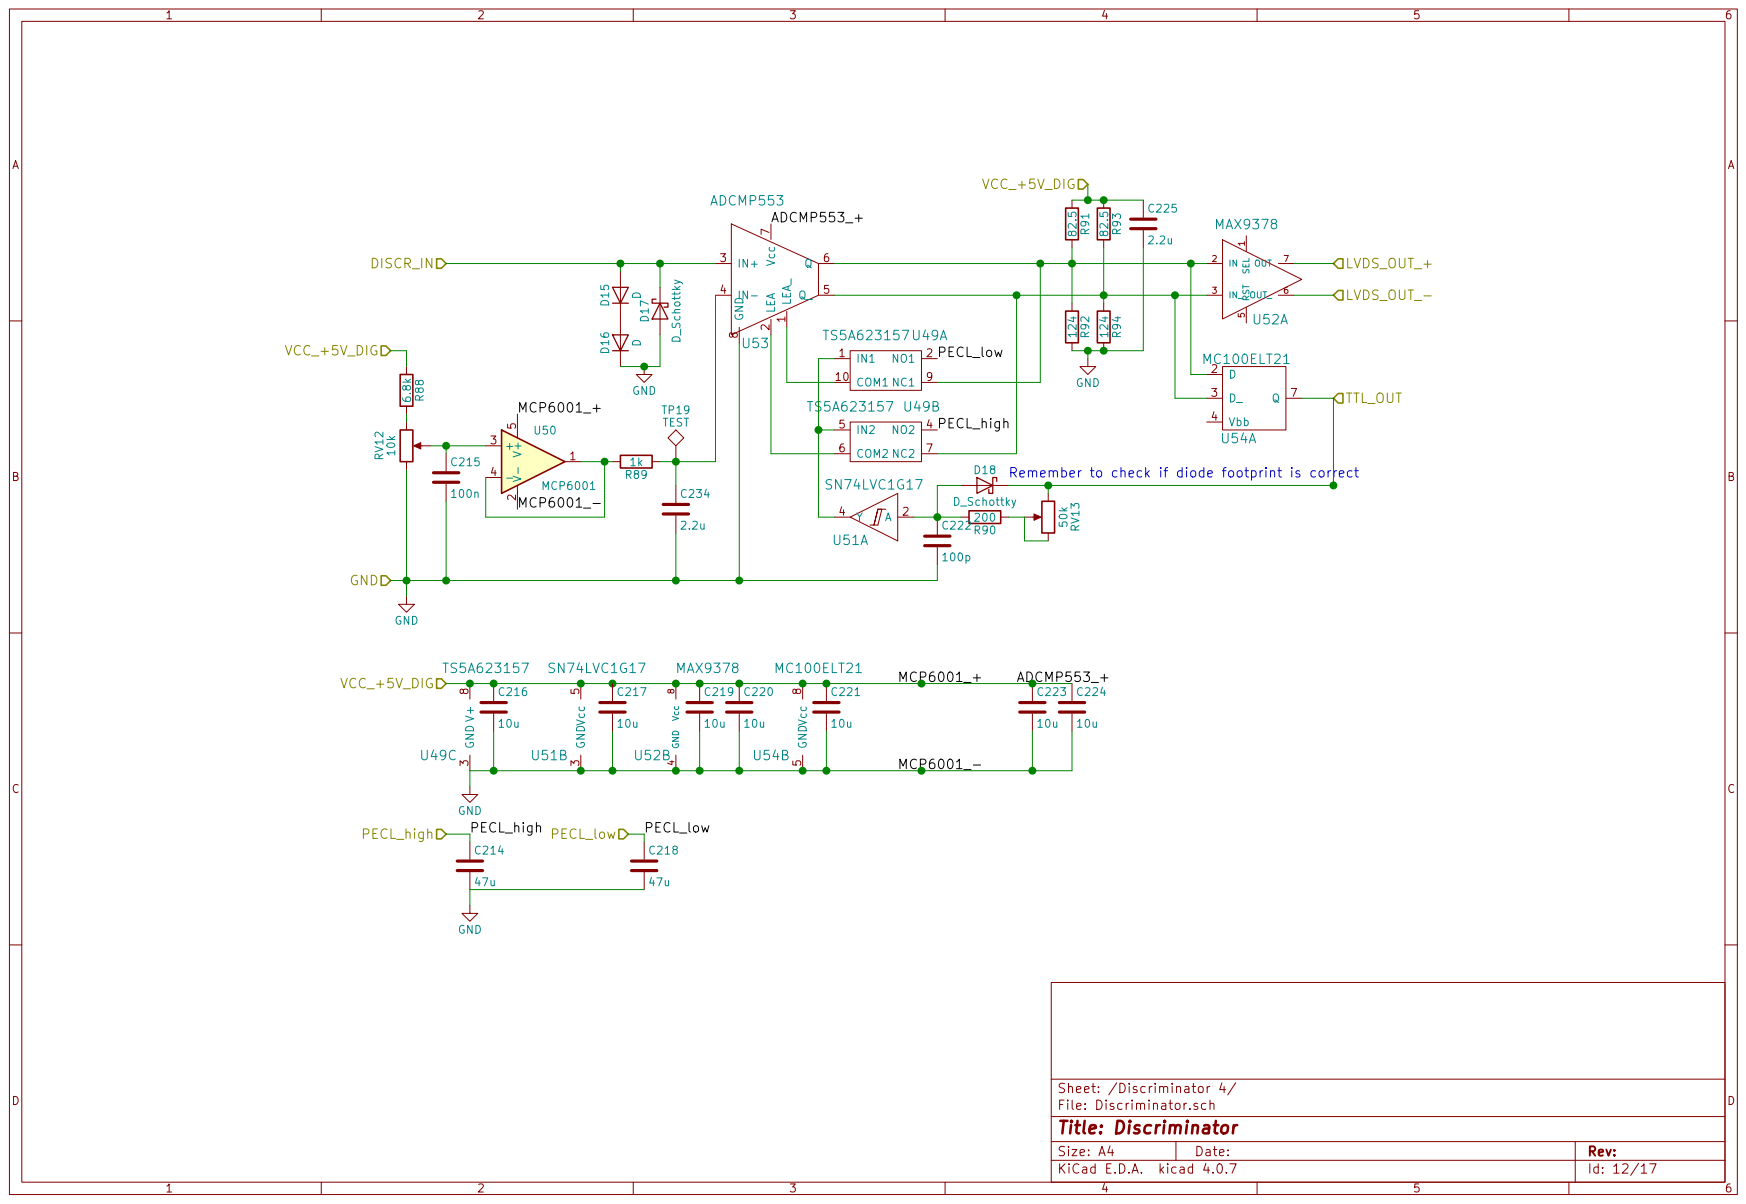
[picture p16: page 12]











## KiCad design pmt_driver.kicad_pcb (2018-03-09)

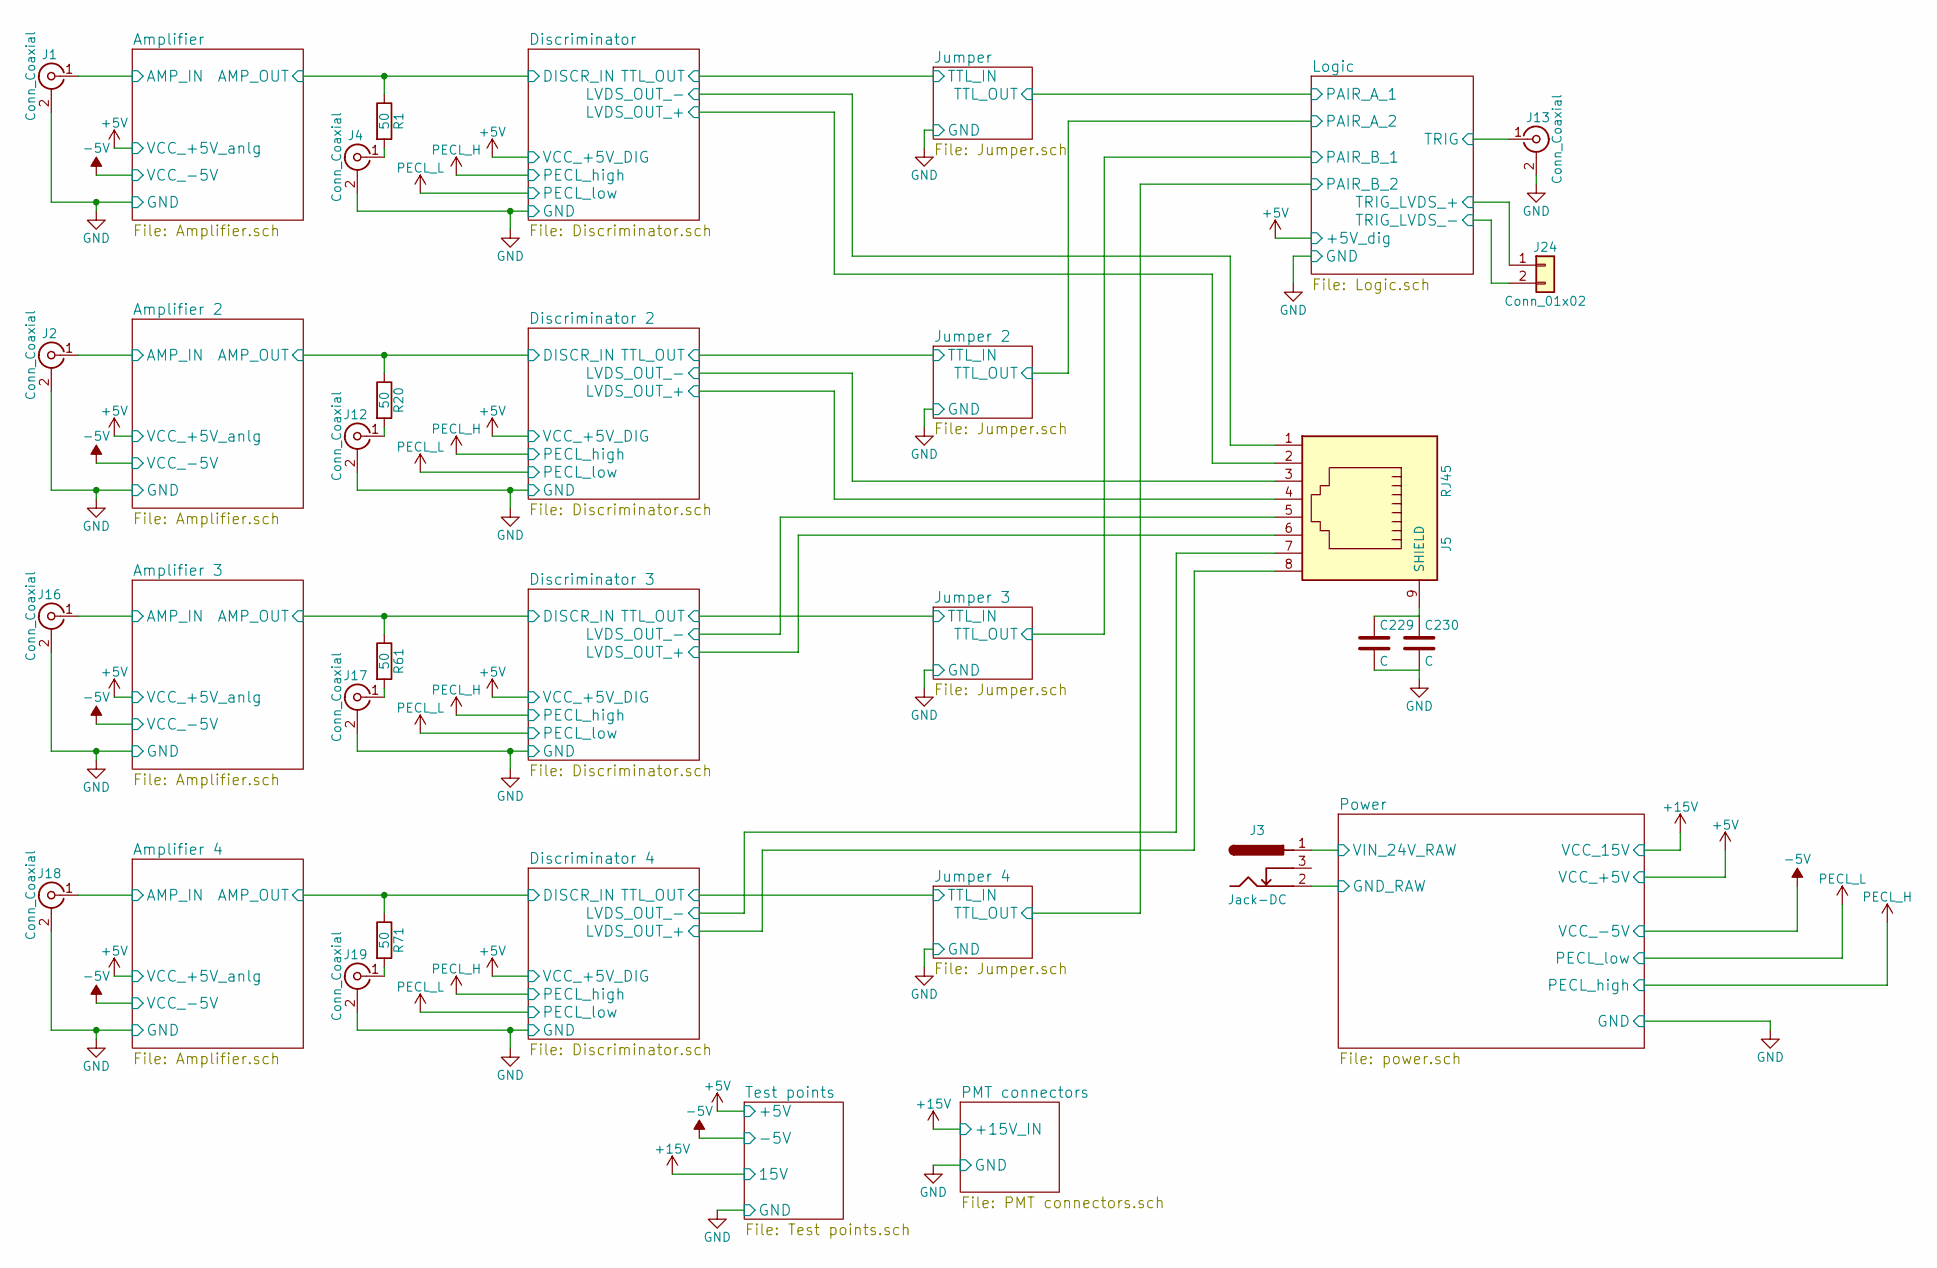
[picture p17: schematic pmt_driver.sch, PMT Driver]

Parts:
C229, C230: C; C_0805
J1, J2, J13, J16, J18: Conn_Coaxial; LEMO_angled; MPN EPK.00.250.NTN
J3: Jack-DC; BARREL_JACK_PJ102B; MPN PJ-102B
J4, J12, J17, J19: Conn_Coaxial; LEMO_straight; MPN EPA.00.250.NTN
J5: RJ45; RJ45_8_A00-108-262-450; MPN A00-108-262-450
J24: Conn_01x02; Pin_Header_Angled_1x02_Pitch2.54mm; MPN 640455-2
R1, R20, R61, R71: 50; R_0805

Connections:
/Amplifier 2/AMP_IN: J2.1 (In); also elsewhere on the board
/Amplifier 2/AMP_OUT: R20.1; also elsewhere on the board
/Amplifier 3/AMP_IN: J16.1 (In); also elsewhere on the board
/Amplifier 3/AMP_OUT: R61.1; also elsewhere on the board
/Amplifier 4/AMP_IN: J18.1 (In); also elsewhere on the board
/Amplifier 4/AMP_OUT: R71.1; also elsewhere on the board
/Amplifier/AMP_IN: J1.1 (In); also elsewhere on the board
/Amplifier/AMP_OUT: R1.1; also elsewhere on the board
/Discriminator 2/LVDS_OUT_+: J5.4; also elsewhere on the board
/Discriminator 2/LVDS_OUT_-: J5.3; also elsewhere on the board
/Discriminator 3/LVDS_OUT_+: J5.6; also elsewhere on the board
/Discriminator 3/LVDS_OUT_-: J5.5; also elsewhere on the board
/Discriminator 4/LVDS_OUT_+: J5.8; also elsewhere on the board
/Discriminator 4/LVDS_OUT_-: J5.7; also elsewhere on the board
/Discriminator/LVDS_OUT_+: J5.2; also elsewhere on the board
/Discriminator/LVDS_OUT_-: J5.1; also elsewhere on the board
/Logic/TRIG: J13.1 (In); also elsewhere on the board
/Logic/TRIG_LVDS_+: J24.1; also elsewhere on the board
/Logic/TRIG_LVDS_-: J24.2; also elsewhere on the board
/Power/GND_RAW: J3.2; also elsewhere on the board
/Power/VIN_24V_RAW: J3.1; also elsewhere on the board
GND: C229.2, C230.2, J1.2 (Ext), J2.2 (Ext), J4.2 (Ext), J12.2 (Ext), J13.2 (Ext), J16.2 (Ext), J17.2 (Ext), J18.2 (Ext), J19.2 (Ext); also elsewhere on the board
unnamed: C229.1, C230.1, J5.9 (SHIELD)
unnamed: J4.1 (In), R1.2
unnamed: J12.1 (In), R20.2
unnamed: J17.1 (In), R61.2
unnamed: J19.1 (In), R71.2

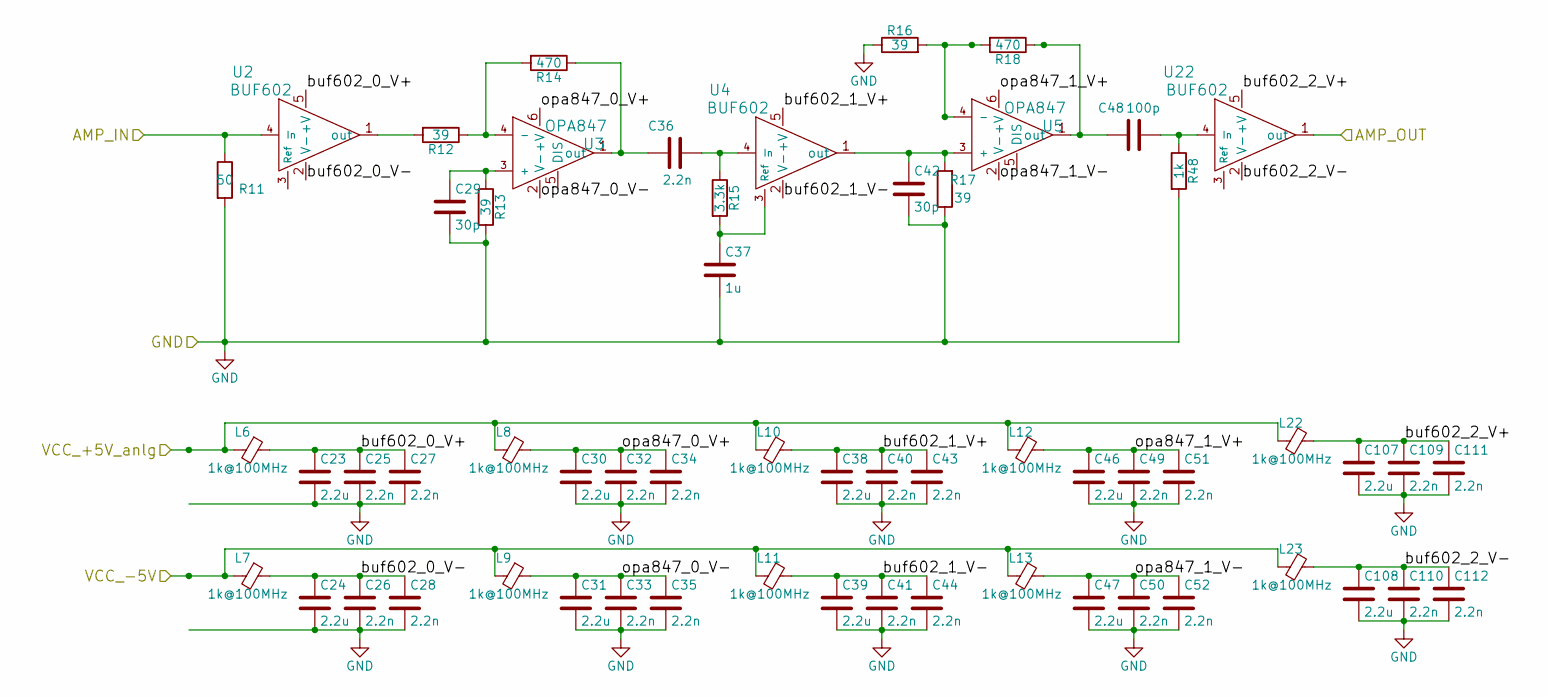
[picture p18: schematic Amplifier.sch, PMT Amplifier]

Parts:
C23, C24, C30, C31, C38, C39, C46, C47, C107, C108: 2.2u; C_0402; MPN GRM155R61C225KE11DDDD
C25, C26, C27, C28, C32, C33, C34, C35, C36, C40, C41, C43, C44, C49, C50, C51, C52, C109, C110, C111, C112: 2.2n; C_0306; MPN LLL185R71H222MA01
C29, C42: 30p; C_0603; MPN GRM0335C1H300JA01D
C37: 1u; C_0603
C48: 100p; C_0603; MPN C0603C101J5GACTU
L6, L7, L8, L9, L10, L11, L12, L13, L22, L23: 1k@100MHz; L_1210; MPN FB MH3225HM601NT
R11: 50; R_0805
R12, R13, R16, R17: 39; R_0603; MPN RC0603FR-0739RL
R14: 470; R_0603; MPN RC0603FR-07470RL
R15: 3.3k; C_0805
R18: 470; R_0402; MPN RC0402FR-07470RL
R48: 1k; C_0805
U2, U4, U22: BUF602; SOT-23-5; MPN BUF602IDBVT
U3, U5: OPA847; SOT-23-6; MPN OPA847IDBVT

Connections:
+5V: L6.2, L8.2, L10.2, L12.2, L22.2; also elsewhere on the board
-5V: L7.2, L9.2, L11.2, L13.2, L23.2; also elsewhere on the board
/Amplifier/AMP_IN: R11.1, U2.4 (In); also elsewhere on the board
/Amplifier/AMP_OUT: U22.1 (out); also elsewhere on the board
/Amplifier/buf602_0_V+: C23.1, C25.1, C27.1, L6.1, U2.5 (+V)
/Amplifier/buf602_0_V-: C24.1, C26.1, C28.1, L7.1, U2.2 (V-)
/Amplifier/buf602_1_V+: C38.1, C40.1, C43.1, L10.1, U4.5 (+V)
/Amplifier/buf602_1_V-: C39.1, C41.1, C44.1, L11.1, U4.2 (V-)
/Amplifier/buf602_2_V+: C107.1, C109.1, C111.1, L22.1, U22.5 (+V)
/Amplifier/buf602_2_V-: C108.1, C110.1, C112.1, L23.1, U22.2 (V-)
/Amplifier/opa847_0_V+: C30.1, C32.1, C34.1, L8.1, U3.6 (+V)
/Amplifier/opa847_0_V-: C31.1, C33.1, C35.1, L9.1, U3.2 (V-)
/Amplifier/opa847_1_V+: C46.1, C49.1, C51.1, L12.1, U5.6 (+V)
/Amplifier/opa847_1_V-: C47.1, C50.1, C52.1, L13.1, U5.2 (V-)
GND: C23.2, C24.2, C25.2, C26.2, C27.2, C28.2, C29.2, C30.2, C31.2, C32.2, C33.2, C34.2, C35.2, C37.2, C38.2, C39.2, C40.2, C41.2, C42.2, C43.2, C44.2, C46.2, C47.2, C49.2, C50.2, C51.2, C52.2, C107.2, C108.2, C109.2, C110.2, C111.2, C112.2, R11.2, R13.2, R16.1, R17.1, R48.2; also elsewhere on the board
unnamed: C29.1, R13.1, U3.3 (+)
unnamed: C36.1, R14.1, U3.1 (out)
unnamed: C36.2, R15.1, U4.4 (In)
unnamed: C37.1, R15.2, U4.3 (Ref)
unnamed: C42.1, R17.2, U4.1 (out), U5.3 (+)
unnamed: C48.1, R18.1, U5.1 (out)
unnamed: C48.2, R48.1, U22.4 (In)
unnamed: R12.1, R14.2, U3.4 (-)
unnamed: R12.2, U2.1 (out)
unnamed: R16.2, R18.2, U5.4 (-)

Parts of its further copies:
C76, C77, C78, C84, C85, C92, C93, C100, C101, C113, C114, C131, C137, C138, C145, C146, C153, C154, C160, C161, C166, C167, C173, C174, C181, C182, C189, C190, C196, C197: 2.2u; C_0402; MPN GRM155R61C225KE11DDDD
C79, C80, C81, C82, C86, C87, C88, C89, C90, C94, C95, C97, C98, C103, C104, C105, C106, C115, C116, C117, C118, C132, C133, C134, C135, C139, C140, C141, C142, C143, C147, C148, C150, C151, C156, C157, C158, C159, C162, C163, C164, C165, C168, C169, C170, C171, C175, C176, C177, C178, C179, C183, C184, C186, C187, C192, C193, C194, C195, C198, C199, C200, C201: 2.2n; C_0306; MPN LLL185R71H222MA01
C83, C96, C136, C149, C172, C185: 30p; C_0603; MPN GRM0335C1H300JA01D
C91, C144, C180: 1u; C_0603
C102, C155, C191: 100p; C_0603; MPN C0603C101J5GACTU
L14, L15, L16, L17, L18, L19, L20, L21, L24, L25, L26, L27, L28, L29, L30, L31, L32, L33, L34, L35, L36, L37, L38, L39, L40, L41, L42, L43, L44, L45: 1k@100MHz; L_1210; MPN FB MH3225HM601NT
R40, R62, R72: 50; R_0805
R41, R42, R45, R46, R63, R64, R67, R68, R73, R74, R77, R78: 39; R_0603; MPN RC0603FR-0739RL
R43, R65, R75: 470; R_0603; MPN RC0603FR-07470RL
R44, R66, R76: 3.3k; C_0805
R47, R69, R79: 470; R_0402; MPN RC0402FR-07470RL
R49, R70, R80: 1k; C_0805
U18, U20, U23, U33, U35, U37, U38, U40, U42: BUF602; SOT-23-5; MPN BUF602IDBVT
U19, U21, U34, U36, U39, U41: OPA847; SOT-23-6; MPN OPA847IDBVT

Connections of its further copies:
+5V: L14.2, L16.2, L18.2, L20.2, L24.2, L26.2, L28.2, L30.2, L32.2, L34.2, L36.2, L38.2, L40.2, L42.2, L44.2; also elsewhere on the board
-5V: L15.2, L17.2, L19.2, L21.2, L25.2, L27.2, L29.2, L31.2, L33.2, L35.2, L37.2, L39.2, L41.2, L43.2, L45.2; also elsewhere on the board
/Amplifier 2/AMP_IN: R40.1, U18.4 (In); also elsewhere on the board
/Amplifier 2/AMP_OUT: U23.1 (out); also elsewhere on the board
/Amplifier 2/buf602_0_V+: C77.1, C79.1, C81.1, L14.1, U18.5 (+V)
/Amplifier 2/buf602_0_V-: C78.1, C80.1, C82.1, L15.1, U18.2 (V-)
/Amplifier 2/buf602_1_V+: C92.1, C94.1, C97.1, L18.1, U20.5 (+V)
/Amplifier 2/buf602_1_V-: C93.1, C95.1, C98.1, L19.1, U20.2 (V-)
/Amplifier 2/buf602_2_V+: C113.1, C115.1, C117.1, L24.1, U23.5 (+V)
/Amplifier 2/buf602_2_V-: C114.1, C116.1, C118.1, L25.1, U23.2 (V-)
/Amplifier 2/opa847_0_V+: C84.1, C86.1, C88.1, L16.1, U19.6 (+V)
/Amplifier 2/opa847_0_V-: C85.1, C87.1, C89.1, L17.1, U19.2 (V-)
/Amplifier 2/opa847_1_V+: C100.1, C103.1, C105.1, L20.1, U21.6 (+V)
/Amplifier 2/opa847_1_V-: C101.1, C104.1, C106.1, L21.1, U21.2 (V-)
/Amplifier 3/AMP_IN: R62.1, U33.4 (In); also elsewhere on the board
/Amplifier 3/AMP_OUT: U37.1 (out); also elsewhere on the board
/Amplifier 3/buf602_0_V+: C76.1, C132.1, C134.1, L26.1, U33.5 (+V)
/Amplifier 3/buf602_0_V-: C131.1, C133.1, C135.1, L27.1, U33.2 (V-)
/Amplifier 3/buf602_1_V+: C145.1, C147.1, C150.1, L30.1, U35.5 (+V)
/Amplifier 3/buf602_1_V-: C146.1, C148.1, C151.1, L31.1, U35.2 (V-)
/Amplifier 3/buf602_2_V+: C160.1, C162.1, C164.1, L34.1, U37.5 (+V)
/Amplifier 3/buf602_2_V-: C161.1, C163.1, C165.1, L35.1, U37.2 (V-)
/Amplifier 3/opa847_0_V+: C137.1, C139.1, C141.1, L28.1, U34.6 (+V)
/Amplifier 3/opa847_0_V-: C138.1, C140.1, C142.1, L29.1, U34.2 (V-)
/Amplifier 3/opa847_1_V+: C153.1, C156.1, C158.1, L32.1, U36.6 (+V)
/Amplifier 3/opa847_1_V-: C154.1, C157.1, C159.1, L33.1, U36.2 (V-)
/Amplifier 4/AMP_IN: R72.1, U38.4 (In); also elsewhere on the board
/Amplifier 4/AMP_OUT: U42.1 (out); also elsewhere on the board
/Amplifier 4/buf602_0_V+: C166.1, C168.1, C170.1, L36.1, U38.5 (+V)
/Amplifier 4/buf602_0_V-: C167.1, C169.1, C171.1, L37.1, U38.2 (V-)
/Amplifier 4/buf602_1_V+: C181.1, C183.1, C186.1, L40.1, U40.5 (+V)
/Amplifier 4/buf602_1_V-: C182.1, C184.1, C187.1, L41.1, U40.2 (V-)
/Amplifier 4/buf602_2_V+: C196.1, C198.1, C200.1, L44.1, U42.5 (+V)
/Amplifier 4/buf602_2_V-: C197.1, C199.1, C201.1, L45.1, U42.2 (V-)
/Amplifier 4/opa847_0_V+: C173.1, C175.1, C177.1, L38.1, U39.6 (+V)
/Amplifier 4/opa847_0_V-: C174.1, C176.1, C178.1, L39.1, U39.2 (V-)
/Amplifier 4/opa847_1_V+: C189.1, C192.1, C194.1, L42.1, U41.6 (+V)
/Amplifier 4/opa847_1_V-: C190.1, C193.1, C195.1, L43.1, U41.2 (V-)
GND: C76.2, C77.2, C78.2, C79.2, C80.2, C81.2, C82.2, C83.2, C84.2, C85.2, C86.2, C87.2, C88.2, C89.2, C91.2, C92.2, C93.2, C94.2, C95.2, C96.2, C97.2, C98.2, C100.2, C101.2, C103.2, C104.2, C105.2, C106.2, C113.2, C114.2, C115.2, C116.2, C117.2, C118.2, C131.2, C132.2, C133.2, C134.2, C135.2, C136.2, C137.2, C138.2, C139.2, C140.2, C141.2, C142.2, C144.2, C145.2, C146.2, C147.2, C148.2, C149.2, C150.2, C151.2, C153.2, C154.2, C156.2, C157.2, C158.2, C159.2, C160.2, C161.2, C162.2, C163.2, C164.2, C165.2, C166.2, C167.2, C168.2, C169.2, C170.2, C171.2, C172.2, C173.2, C174.2, C175.2, C176.2, C177.2, C178.2, C180.2, C181.2, C182.2, C183.2, C184.2, C185.2, C186.2, C187.2, C189.2, C190.2, C192.2, C193.2, C194.2, C195.2, C196.2, C197.2, C198.2, C199.2, C200.2, C201.2, R40.2, R42.2, R45.1, R46.1, R49.2, R62.2, R64.2, R67.1, R68.1, R70.2, R72.2, R74.2, R77.1, R78.1, R80.2; also elsewhere on the board
unnamed: C83.1, R42.1, U19.3 (+)
unnamed: C90.1, R43.1, U19.1 (out)
unnamed: C90.2, R44.1, U20.4 (In)
unnamed: C91.1, R44.2, U20.3 (Ref)
unnamed: C96.1, R46.2, U20.1 (out), U21.3 (+)
unnamed: C102.1, R47.1, U21.1 (out)
unnamed: C102.2, R49.1, U23.4 (In)
unnamed: C136.1, R64.1, U34.3 (+)
unnamed: C143.1, R65.1, U34.1 (out)
unnamed: C143.2, R66.1, U35.4 (In)
unnamed: C144.1, R66.2, U35.3 (Ref)
unnamed: C149.1, R68.2, U35.1 (out), U36.3 (+)
unnamed: C155.1, R69.1, U36.1 (out)
unnamed: C155.2, R70.1, U37.4 (In)
unnamed: C172.1, R74.1, U39.3 (+)
unnamed: C179.1, R75.1, U39.1 (out)
unnamed: C179.2, R76.1, U40.4 (In)
unnamed: C180.1, R76.2, U40.3 (Ref)
unnamed: C185.1, R78.2, U40.1 (out), U41.3 (+)
unnamed: C191.1, R79.1, U41.1 (out)
unnamed: C191.2, R80.1, U42.4 (In)
unnamed: R41.1, R43.2, U19.4 (-)
unnamed: R41.2, U18.1 (out)
unnamed: R45.2, R47.2, U21.4 (-)
unnamed: R63.1, R65.2, U34.4 (-)
unnamed: R63.2, U33.1 (out)
unnamed: R67.2, R69.2, U36.4 (-)
unnamed: R73.1, R75.2, U39.4 (-)
unnamed: R73.2, U38.1 (out)
unnamed: R77.2, R79.2, U41.4 (-)

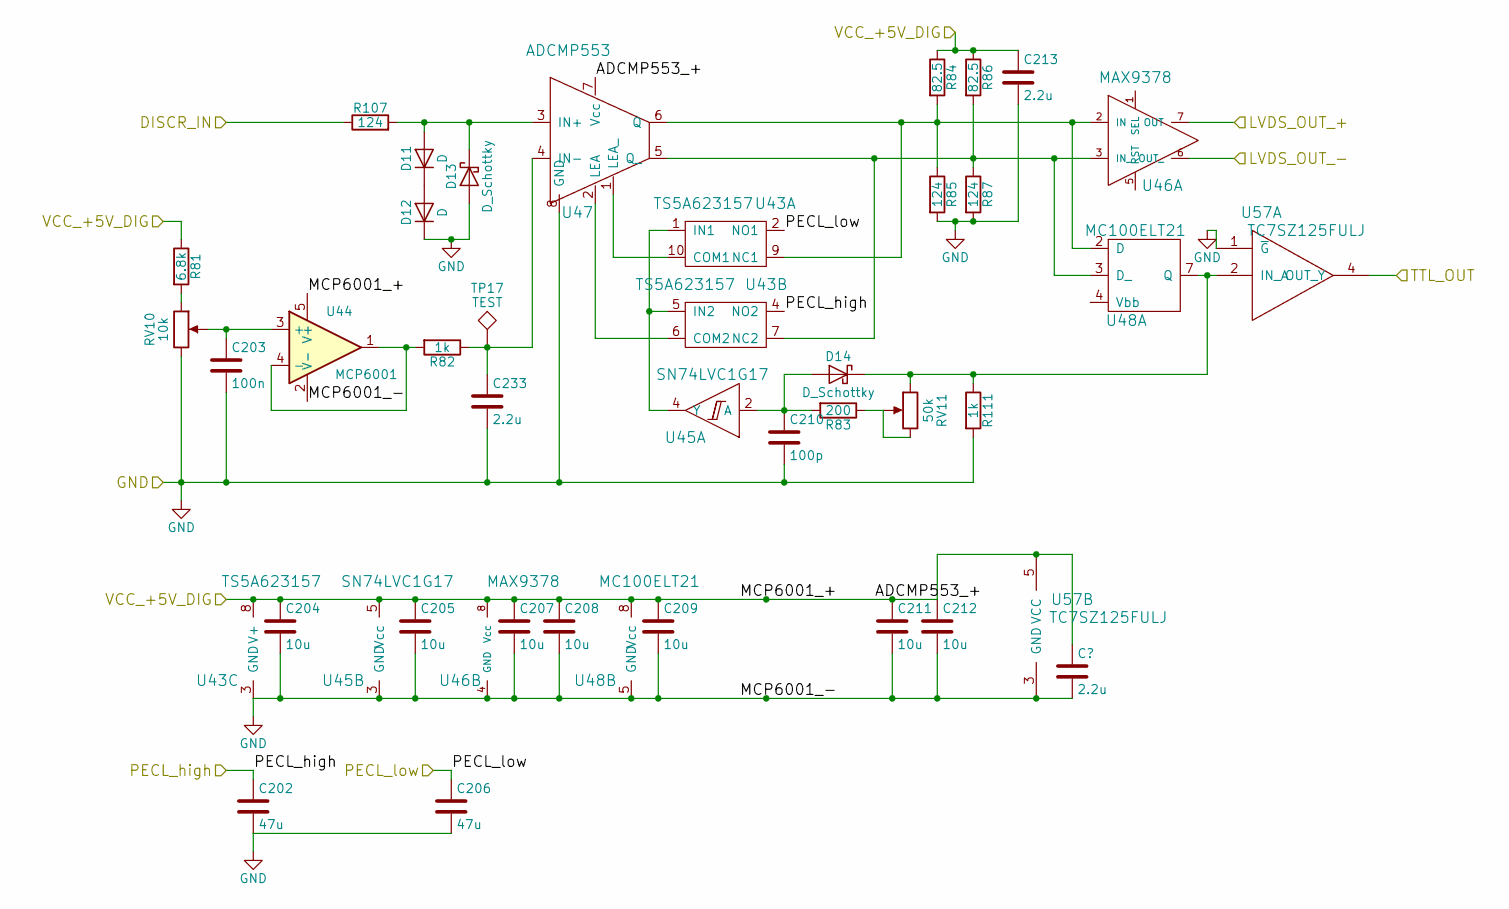
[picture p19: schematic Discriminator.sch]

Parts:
C53, C57: 47u; R_0805_HandSoldering
C54: 100n; C_0603
C55, C56, C58, C59, C60, C62, C63: 10u; R_0612; MPN LLL31MR70J475MA01L
C61: 100p; C_0603; MPN C0603C101J5GACTU
C64, C231: 2.2u; C_0402_NoSilk; MPN GRM155R61C225KE11DDDD
D3, D4: D; SOD-523; MPN 1SS387,L3F
D5, D6: D_Schottky; D_MiniMELF; MPN LL101C-GS08
R19: 6.8k; R_0805
R22, R109: 1k; R_0805
R23: 200; R_0805
R24, R26: 82.5; R_0603; MPN RC0603FR-0782R5L
R25, R27, R105: 124; R_0603; MPN RC0603FR-07124RL
RV1: 10k; Potentiometer_Trimmer_Bourns_3266W; MPN 3266W-1-103LF
RV2: 50k; Potentiometer_Trimmer_Bourns_3266W; MPN 3266W-1-503LF
TP13: TEST; Testpoint_Keystone_11011; MPN 11011-R
U6: TS5A623157; MSOP-10_3x3mm_Pitch0.5mm; MPN TS5A62315DGSR
U7: MCP6001; SOT-23-5_HandSoldering; MPN MCP6001T-I/OT
U8: SN74LVC1G17; SOT-23-5_HandSoldering; MPN SN74LVC1G17DBVR
U9: MAX9378; TSSOP-8_3x3mm_Pitch0.65mm; MPN MAX9378EUA+
U10: ADCMP553; MSOP-8_3x3mm_Pitch0.65mm; MPN ADCMP553BRMZ
U11: MC100ELT21; SOIC-8_3.9x4.9mm_Pitch1.27mm; MPN MC100ELT21DG
U31: TC7SZ125FULJ; SOT-353_SC-70-5

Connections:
+5V: C55.1, C56.1, C58.1, C59.1, C60.1, C62.1, C63.1, C64.1, R19.1, R24.1, R26.1, U6.8 (V+), U7.5 (V+), U8.5 (Vcc), U9.8 (Vcc), U10.7 (Vcc), U11.8 (Vcc), U31.5 (VCC); also elsewhere on the board
/Amplifier/AMP_OUT: R105.1; also elsewhere on the board
/Discriminator/LVDS_OUT_+: U9.7 (OUT); also elsewhere on the board
/Discriminator/LVDS_OUT_-: U9.6 (OUT_); also elsewhere on the board
/Jumper/TTL_IN: U31.4 (OUT_Y); also elsewhere on the board
GND: C53.2, C54.2, C55.2, C56.2, C57.2, C58.2, C59.2, C60.2, C61.2, C62.2, C63.2, C64.2, C231.2, D4.1 (K), D5.2 (A), R25.2, R27.2, R109.2, RV1.3, U6.3 (GND), U7.2 (V-), U8.3 (GND), U9.4 (GND), U10.8 (GND), U11.5 (GND), U31.1 (~G), U31.3 (GND); also elsewhere on the board
unnamed: C54.1, RV1.2, U7.3 (+)
unnamed: C61.1, D6.2 (A), R23.2, U8.2 (A)
unnamed: C231.1, R22.1, TP13.1, U10.4 (IN-)
unnamed: D3.1 (K), D4.2 (A)
unnamed: D3.2 (A), D5.1 (K), R105.2, U10.3 (IN+)
unnamed: D6.1 (K), R109.1, RV2.1, U11.7 (Q), U31.2 (IN_A)
unnamed: R19.2, RV1.1
unnamed: R22.2, U7.1, U7.4 (-)
unnamed: R23.1, RV2.2, RV2.3
unnamed: R24.2, R25.1, U6.9 (NC1), U9.2 (IN), U10.6 (Q), U11.2 (D)
unnamed: R26.2, R27.1, U6.7 (NC2), U9.3 (IN_), U10.5 (Q_), U11.3 (D_)
unnamed: U6.1 (IN1), U6.5 (IN2), U8.4 (Y)
unnamed: U6.10 (COM1), U10.1 (LEA_)
unnamed: U6.6 (COM2), U10.2 (LEA)
PECL_high: C53.1, U6.4 (NO2); also elsewhere on the board
PECL_low: C57.1, U6.2 (NO1); also elsewhere on the board

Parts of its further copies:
C119, C123, C202, C206, C214, C218: 47u; R_0805_HandSoldering
C120, C203, C215: 100n; C_0603
C121, C122, C124, C125, C126, C128, C129, C204, C205, C207, C208, C209, C211, C212, C216, C217, C219, C220, C221, C223, C224: 10u; R_0612; MPN LLL31MR70J475MA01L
C127, C210, C222: 100p; C_0603; MPN C0603C101J5GACTU
C130, C213, C225, C232, C233, C234: 2.2u; C_0402_NoSilk; MPN GRM155R61C225KE11DDDD
D7, D8, D11, D12, D15, D16: D; SOD-523; MPN 1SS387,L3F
D9, D10, D13, D14, D17, D18: D_Schottky; D_MiniMELF; MPN LL101C-GS08
R21, R81, R88: 6.8k; R_0805
R50, R82, R89, R110, R111, R112: 1k; R_0805
R51, R83, R90: 200; R_0805
R52, R54, R84, R86, R91, R93: 82.5; R_0603; MPN RC0603FR-0782R5L
R53, R55, R85, R87, R92, R94, R106, R107, R108: 124; R_0603; MPN RC0603FR-07124RL
RV7, RV10, RV12: 10k; Potentiometer_Trimmer_Bourns_3266W; MPN 3266W-1-103LF
RV8, RV11, RV13: 50k; Potentiometer_Trimmer_Bourns_3266W; MPN 3266W-1-503LF
TP15, TP17, TP19: TEST; Testpoint_Keystone_11011; MPN 11011-R
U24, U43, U49: TS5A623157; MSOP-10_3x3mm_Pitch0.5mm; MPN TS5A62315DGSR
U25, U44, U50: MCP6001; SOT-23-5_HandSoldering; MPN MCP6001T-I/OT
U26, U45, U51: SN74LVC1G17; SOT-23-5_HandSoldering; MPN SN74LVC1G17DBVR
U27, U46, U52: MAX9378; TSSOP-8_3x3mm_Pitch0.65mm; MPN MAX9378EUA+
U28, U47, U53: ADCMP553; MSOP-8_3x3mm_Pitch0.65mm; MPN ADCMP553BRMZ
U29, U48, U54: MC100ELT21; SOIC-8_3.9x4.9mm_Pitch1.27mm; MPN MC100ELT21DG
U56, U57, U58: TC7SZ125FULJ; SOT-353_SC-70-5

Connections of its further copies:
+5V: C121.1, C122.1, C124.1, C125.1, C126.1, C128.1, C129.1, C130.1, C204.1, C205.1, C207.1, C208.1, C209.1, C211.1, C212.1, C213.1, C216.1, C217.1, C219.1, C220.1, C221.1, C223.1, C224.1, C225.1, R21.1, R52.1, R54.1, R81.1, R84.1, R86.1, R88.1, R91.1, R93.1, U24.8 (V+), U25.5 (V+), U26.5 (Vcc), U27.8 (Vcc), U28.7 (Vcc), U29.8 (Vcc), U43.8 (V+), U44.5 (V+), U45.5 (Vcc), U46.8 (Vcc), U47.7 (Vcc), U48.8 (Vcc), U49.8 (V+), U50.5 (V+), U51.5 (Vcc), U52.8 (Vcc), U53.7 (Vcc), U54.8 (Vcc), U56.5 (VCC), U57.5 (VCC), U58.5 (VCC); also elsewhere on the board
/Amplifier 2/AMP_OUT: R106.1; also elsewhere on the board
/Amplifier 3/AMP_OUT: R107.1; also elsewhere on the board
/Amplifier 4/AMP_OUT: R108.1; also elsewhere on the board
/Discriminator 2/LVDS_OUT_+: U27.7 (OUT); also elsewhere on the board
/Discriminator 2/LVDS_OUT_-: U27.6 (OUT_); also elsewhere on the board
/Discriminator 3/LVDS_OUT_+: U46.7 (OUT); also elsewhere on the board
/Discriminator 3/LVDS_OUT_-: U46.6 (OUT_); also elsewhere on the board
/Discriminator 4/LVDS_OUT_+: U52.7 (OUT); also elsewhere on the board
/Discriminator 4/LVDS_OUT_-: U52.6 (OUT_); also elsewhere on the board
/Jumper 2/TTL_IN: U56.4 (OUT_Y); also elsewhere on the board
/Jumper 3/TTL_IN: U57.4 (OUT_Y); also elsewhere on the board
/Jumper 4/TTL_IN: U58.4 (OUT_Y); also elsewhere on the board
GND: C119.2, C120.2, C121.2, C122.2, C123.2, C124.2, C125.2, C126.2, C127.2, C128.2, C129.2, C130.2, C202.2, C203.2, C204.2, C205.2, C206.2, C207.2, C208.2, C209.2, C210.2, C211.2, C212.2, C213.2, C214.2, C215.2, C216.2, C217.2, C218.2, C219.2, C220.2, C221.2, C222.2, C223.2, C224.2, C225.2, C232.2, C233.2, C234.2, D8.1 (K), D9.2 (A), D12.1 (K), D13.2 (A), D16.1 (K), D17.2 (A), R53.2, R55.2, R85.2, R87.2, R92.2, R94.2, R110.2, R111.2, R112.2, RV7.3, RV10.3, RV12.3, U24.3 (GND), U25.2 (V-), U26.3 (GND), U27.4 (GND), U28.8 (GND), U29.5 (GND), U43.3 (GND), U44.2 (V-), U45.3 (GND), U46.4 (GND), U47.8 (GND), U48.5 (GND), U49.3 (GND), U50.2 (V-), U51.3 (GND), U52.4 (GND), U53.8 (GND), U54.5 (GND), U56.1 (~G), U56.3 (GND), U57.1 (~G), U57.3 (GND), U58.1 (~G), U58.3 (GND); also elsewhere on the board
unnamed: C120.1, RV7.2, U25.3 (+)
unnamed: C127.1, D10.2 (A), R51.2, U26.2 (A)
unnamed: C203.1, RV10.2, U44.3 (+)
unnamed: C210.1, D14.2 (A), R83.2, U45.2 (A)
unnamed: C215.1, RV12.2, U50.3 (+)
unnamed: C222.1, D18.2 (A), R90.2, U51.2 (A)
unnamed: C232.1, R50.1, TP15.1, U28.4 (IN-)
unnamed: C233.1, R82.1, TP17.1, U47.4 (IN-)
unnamed: C234.1, R89.1, TP19.1, U53.4 (IN-)
unnamed: D7.1 (K), D8.2 (A)
unnamed: D7.2 (A), D9.1 (K), R106.2, U28.3 (IN+)
unnamed: D10.1 (K), R110.1, RV8.1, U29.7 (Q), U56.2 (IN_A)
unnamed: D11.1 (K), D12.2 (A)
unnamed: D11.2 (A), D13.1 (K), R107.2, U47.3 (IN+)
unnamed: D14.1 (K), R111.1, RV11.1, U48.7 (Q), U57.2 (IN_A)
unnamed: D15.1 (K), D16.2 (A)
unnamed: D15.2 (A), D17.1 (K), R108.2, U53.3 (IN+)
unnamed: D18.1 (K), R112.1, RV13.1, U54.7 (Q), U58.2 (IN_A)
unnamed: R21.2, RV7.1
unnamed: R50.2, U25.1, U25.4 (-)
unnamed: R51.1, RV8.2, RV8.3
unnamed: R52.2, R53.1, U24.9 (NC1), U27.2 (IN), U28.6 (Q), U29.2 (D)
unnamed: R54.2, R55.1, U24.7 (NC2), U27.3 (IN_), U28.5 (Q_), U29.3 (D_)
unnamed: R81.2, RV10.1
unnamed: R82.2, U44.1, U44.4 (-)
unnamed: R83.1, RV11.2, RV11.3
unnamed: R84.2, R85.1, U43.9 (NC1), U46.2 (IN), U47.6 (Q), U48.2 (D)
unnamed: R86.2, R87.1, U43.7 (NC2), U46.3 (IN_), U47.5 (Q_), U48.3 (D_)
unnamed: R88.2, RV12.1
unnamed: R89.2, U50.1, U50.4 (-)
unnamed: R90.1, RV13.2, RV13.3
unnamed: R91.2, R92.1, U49.9 (NC1), U52.2 (IN), U53.6 (Q), U54.2 (D)
unnamed: R93.2, R94.1, U49.7 (NC2), U52.3 (IN_), U53.5 (Q_), U54.3 (D_)
unnamed: U24.1 (IN1), U24.5 (IN2), U26.4 (Y)
unnamed: U24.6 (COM2), U28.2 (LEA)
unnamed: U24.10 (COM1), U28.1 (LEA_)
unnamed: U43.1 (IN1), U43.5 (IN2), U45.4 (Y)
unnamed: U43.6 (COM2), U47.2 (LEA)
unnamed: U43.10 (COM1), U47.1 (LEA_)
unnamed: U49.1 (IN1), U49.5 (IN2), U51.4 (Y)
unnamed: U49.6 (COM2), U53.2 (LEA)
unnamed: U49.10 (COM1), U53.1 (LEA_)
PECL_high: C119.1, C202.1, C214.1, U24.4 (NO2), U43.4 (NO2), U49.4 (NO2); also elsewhere on the board
PECL_low: C123.1, C206.1, C218.1, U24.2 (NO1), U43.2 (NO1), U49.2 (NO1); also elsewhere on the board

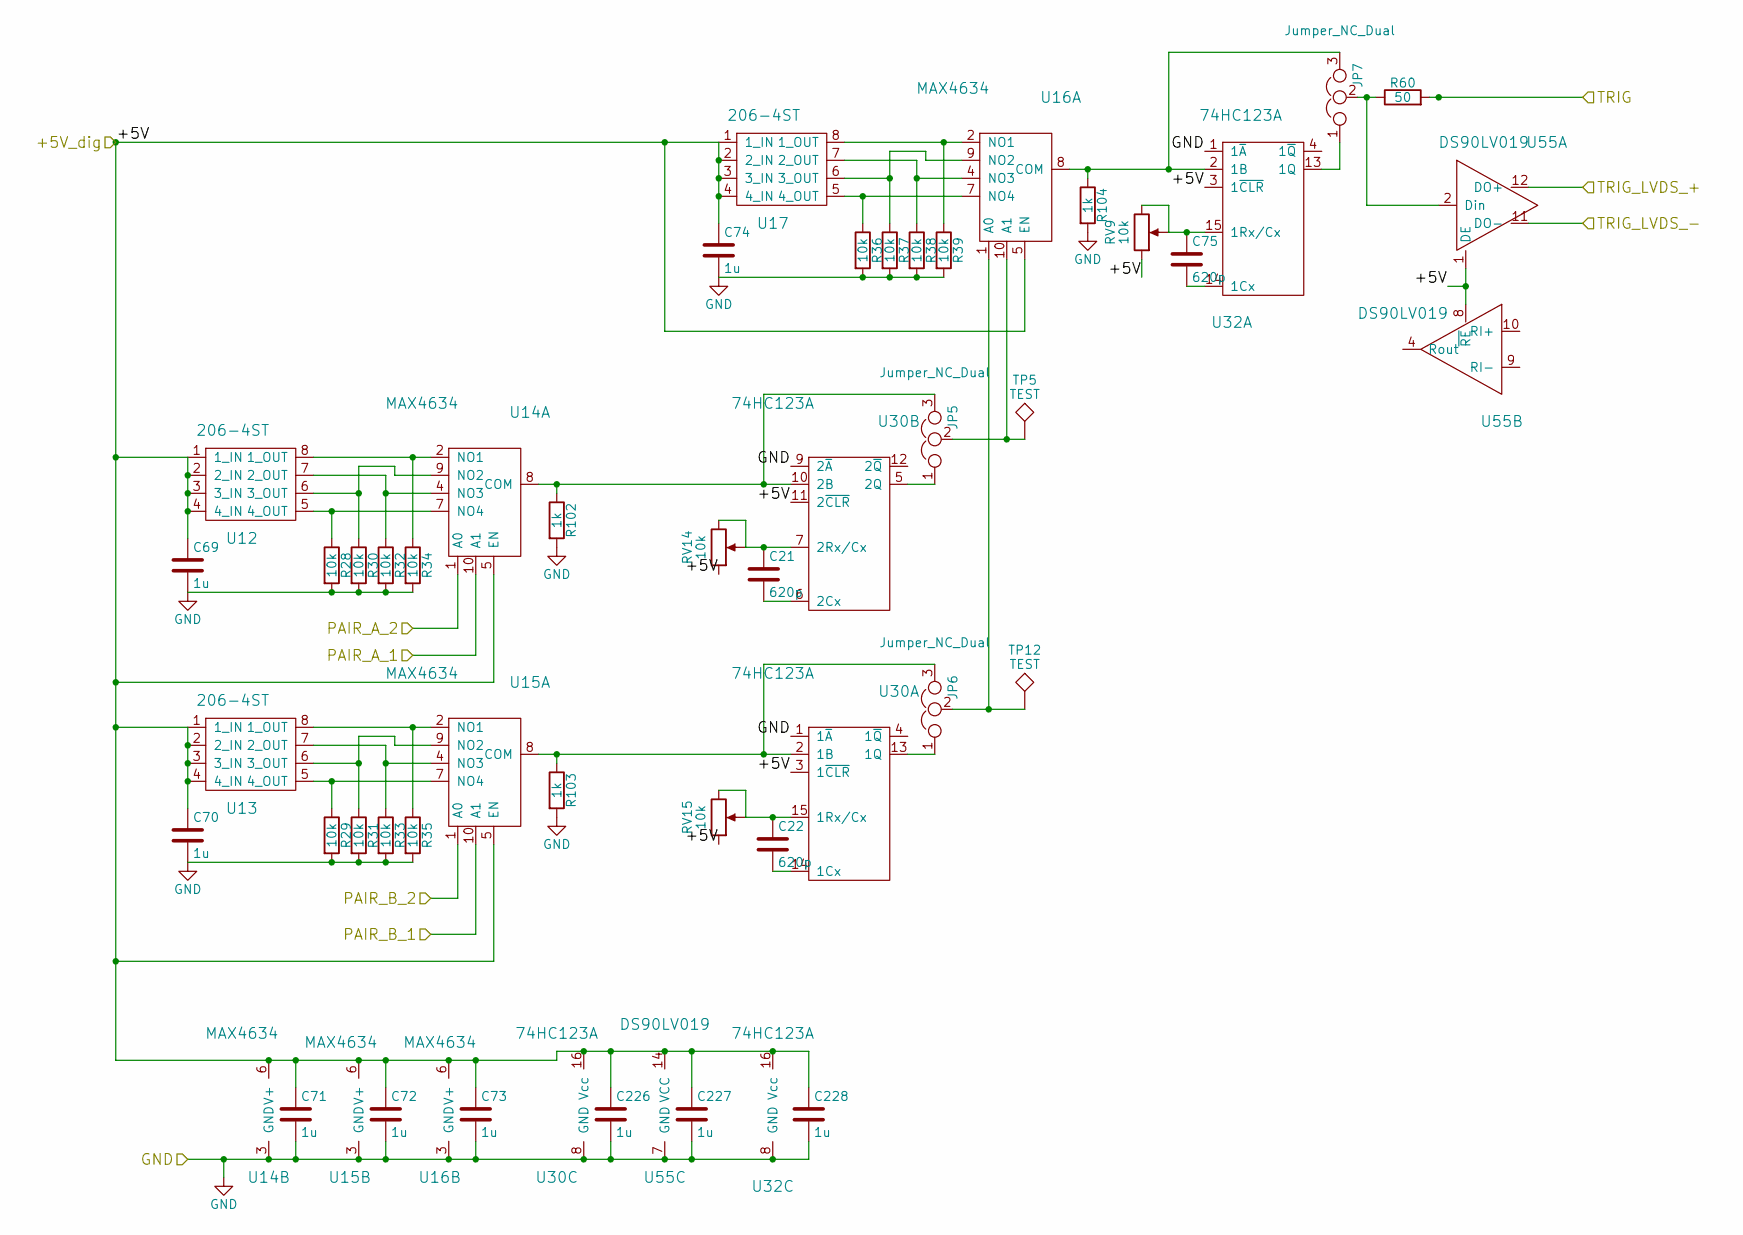
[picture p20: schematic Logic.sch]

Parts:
C21, C22, C75: 620p; C_1206; MPN C1206C621G5GACTU
C69, C70, C71, C72, C73, C74, C226, C227, C228: 1u; C_0603_HandSoldering
JP5, JP6, JP7: Jumper_NC_Dual; Pin_Header_Straight_1x03_Pitch2.54mm
R28, R29, R30, R31, R32, R33, R34, R35, R36, R37, R38, R39: 10k; R_0603_HandSoldering; MPN RC0603JR-0710KL
R60: 50; R_0805
R102, R103, R104: 1k; R_0805
RV9, RV14, RV15: 10k; Potentiometer_Trimmer_Bourns_3266W; MPN 3266W-1-103LF
TP5, TP12: TEST; Testpoint_Keystone_11011; MPN 11011-R
U12, U13, U17: 206-4ST; SW_DIP_x4_W7.62mm_Slide; MPN 206-4ST
U14, U15: MAX4634; MSOP-10_3x3mm_Pitch0.5mm
U16: MAX4634; MSOP-10_3x3mm_Pitch0.5mm; MPN MAX4634EUB+T
U30, U32: 74HC123A; SOIC-16_3.9x9.9mm_Pitch1.27mm; MPN SN74AHCT123AD
U55: DS90LV019; SOIC-14_3.9x8.7mm_Pitch1.27mm

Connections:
+5V: C69.1, C70.1, C71.1, C72.1, C73.1, C74.1, C226.1, C227.1, C228.1, RV9.1, RV14.1, RV15.1, U12.1 (1_IN), U12.2 (2_IN), U12.3 (3_IN), U12.4 (4_IN), U13.1 (1_IN), U13.2 (2_IN), U13.3 (3_IN), U13.4 (4_IN), U14.5 (EN), U14.6 (V+), U15.5 (EN), U15.6 (V+), U16.5 (EN), U16.6 (V+), U17.1 (1_IN), U17.2 (2_IN), U17.3 (3_IN), U17.4 (4_IN), U30.3 (1~CLR), U30.11 (2~CLR), U30.16 (Vcc), U32.3 (1~CLR), U32.16 (Vcc), U55.1 (DE), U55.5 (NC), U55.8 (~RE), U55.14 (VCC); also elsewhere on the board
/Logic/PAIR_A_1: U14.10 (A1); also elsewhere on the board
/Logic/PAIR_A_2: U14.1 (A0); also elsewhere on the board
/Logic/PAIR_B_1: U15.10 (A1); also elsewhere on the board
/Logic/PAIR_B_2: U15.1 (A0); also elsewhere on the board
/Logic/TRIG: R60.2; also elsewhere on the board
/Logic/TRIG_LVDS_+: U55.12 (DO+); also elsewhere on the board
/Logic/TRIG_LVDS_-: U55.11 (DO-); also elsewhere on the board
GND: C69.2, C70.2, C71.2, C72.2, C73.2, C74.2, C226.2, C227.2, C228.2, R28.2, R29.2, R30.2, R31.2, R32.2, R33.2, R34.2, R35.2, R36.2, R37.2, R38.2, R39.2, R102.2, R103.2, R104.2, U14.3 (GND), U15.3 (GND), U16.3 (GND), U30.1 (1~A), U30.8 (GND), U30.9 (2~A), U32.1 (1~A), U32.8 (GND), U55.7 (GND); also elsewhere on the board
unnamed: C21.1, RV14.2, RV14.3, U30.7 (2Rx/Cx)
unnamed: C21.2, U30.6 (2Cx)
unnamed: C22.1, RV15.2, RV15.3, U30.15 (1Rx/Cx)
unnamed: C22.2, U30.14 (1Cx)
unnamed: C75.1, RV9.2, RV9.3, U32.15 (1Rx/Cx)
unnamed: C75.2, U32.14 (1Cx)
unnamed: JP5.1, U30.5 (2Q)
unnamed: JP5.2, TP5.1, U16.10 (A1)
unnamed: JP5.3, R102.1, U14.8 (COM), U30.10 (2B)
unnamed: JP6.1, U30.13 (1Q)
unnamed: JP6.2, TP12.1, U16.1 (A0)
unnamed: JP6.3, R103.1, U15.8 (COM), U30.2 (1B)
unnamed: JP7.1, U32.13 (1Q)
unnamed: JP7.2, R60.1, U55.2 (Din)
unnamed: JP7.3, R104.1, U16.8 (COM), U32.2 (1B)
unnamed: R28.1, U12.5 (4_OUT), U14.7 (NO4)
unnamed: R29.1, U13.5 (4_OUT), U15.7 (NO4)
unnamed: R30.1, U12.6 (3_OUT), U14.9 (NO2)
unnamed: R31.1, U13.6 (3_OUT), U15.9 (NO2)
unnamed: R32.1, U12.7 (2_OUT), U14.4 (NO3)
unnamed: R33.1, U13.7 (2_OUT), U15.4 (NO3)
unnamed: R34.1, U12.8 (1_OUT), U14.2 (NO1)
unnamed: R35.1, U13.8 (1_OUT), U15.2 (NO1)
unnamed: R36.1, U16.7 (NO4), U17.5 (4_OUT)
unnamed: R37.1, U16.9 (NO2), U17.6 (3_OUT)
unnamed: R38.1, U16.4 (NO3), U17.7 (2_OUT)
unnamed: R39.1, U16.2 (NO1), U17.8 (1_OUT)

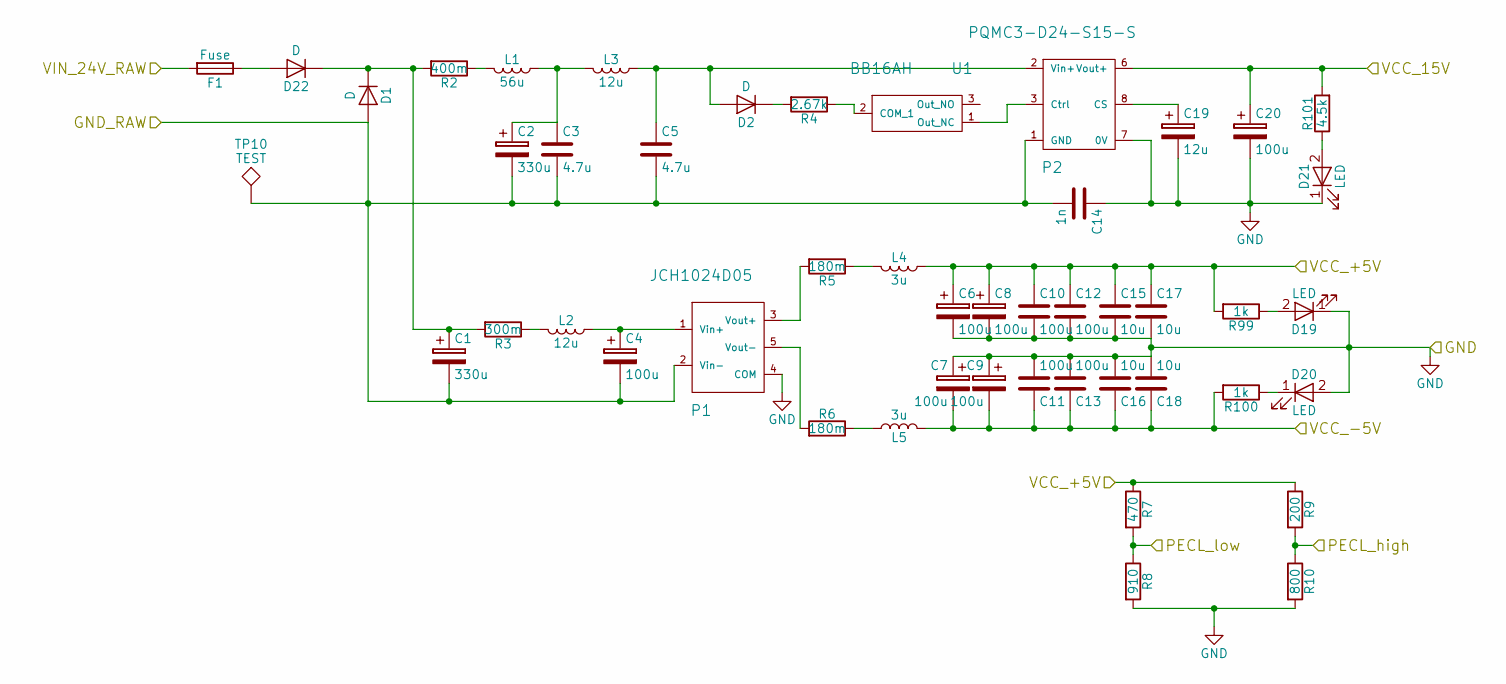
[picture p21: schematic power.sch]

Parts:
C1, C2: 330u; CP_Radial_D10.0mm_P5.00mm; MPN ECA-1HM331
C3, C5: 4.7u; C_1206_HandSoldering; MPN UMK316ABJ475KD-T
C4, C20: 100u; CP_Radial_D8.0mm_P3.50mm; MPN UVz1H101MPD1TD
C6, C7, C8, C9: 100u; CP_Radial_D8.0mm_P5.00mm; MPN EEU-FM1H101B
C10, C11, C12, C13: 100u; C_1206_HandSoldering; MPN C3216X5R1A107M160AC
C14: 1n; R_1206_HandSoldering; MPN 202R18W102KV4E
C15, C16, C17, C18: 10u; C_0805_HandSoldering; MPN C0805C106K8PACTU
C19: 12u; C_Radial_D5_L11_P2; MPN UPW1V120MDD1TP
D1: D; DO-214AB; MPN SMCJ48A
D2: D; D_DO-41_SOD81_P10.16mm_Horizontal
D19, D20, D21: LED; LED_D3.0mm; MPN HLMP-1503-C0002
D22: D; DO-214AB_Handsoldering; MPN S3M
F1: Fuse; Littelfuse_05200101Z_holder; MPN 05200101Z
L1: 56u; L_Toroid_Vertical_L22.4mm_W10.2mm_P7.90mm_Vishay_TJ4; MPN 2210-V-RC
L2: 12u; L_Radial_D10.0mm_P5.00mm_Fastron_07M; MPN RLB0914-120KL
L3: 12u; L_Radial_D6.0mm_P4.00mm; MPN AIUR-07-120K
L4, L5: 3u; L_Radial_D12.0mm_P6.5mm; MPN 74475
P1: JCH1024D05; MPN JCH1024D05
P2: PQMC3-D24-S15-S; PQMC3-S; MPN PQMC3-D24-S15-S
R2: 400m; R_2512; MPN PT2512FK-070R4L
R3: 300m; R_2010_HandSoldering; MPN CSR2010JTR300
R4: 2.67k; R_0805_HandSoldering
R5, R6: 180m; R_1206_HandSoldering; MPN RL1206FR-070R18L
R7: 470; R_0805_HandSoldering
R8: 910; R_0805_HandSoldering
R9: 200; R_0805_HandSoldering
R10: 800; R_0805_HandSoldering
R99, R100: 1k; C_0805
R101: 4.5k; C_0805
TP10: TEST; Test_Point_Keystone_5000-5004_Miniature
U1: BB16AH

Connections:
+5V: C6.1, C8.1, C10.1, C12.1, C15.1, C17.1, L4.1, R7.1, R9.1, R99.2; also elsewhere on the board
+15V: C20.1, P2.6 (Vout+), R101.2; also elsewhere on the board
-5V: C7.2, C9.2, C11.1, C13.1, C16.1, C18.1, L5.1, R100.2; also elsewhere on the board
/Power/GND_RAW: C1.2, C2.2, C3.2, C4.2, C5.2, C14.2, D1.2 (A), P1.2 (Vin-), P2.1 (GND), TP10.1; also elsewhere on the board
/Power/VIN_24V_RAW: F1.2; also elsewhere on the board
GND: C6.2, C7.1, C8.2, C9.1, C10.2, C11.2, C12.2, C13.2, C14.1, C15.2, C16.2, C17.2, C18.2, C19.2, C20.2, D19.1 (K), D20.2 (A), D21.1 (K), P1.4 (COM), P2.7 (0V), R8.2, R10.2; also elsewhere on the board
unnamed: C1.1, D1.1 (K), D22.1 (K), R2.2, R3.2
unnamed: C2.1, C3.1, L1.1, L3.2
unnamed: C4.1, L2.1, P1.1 (Vin+)
unnamed: C5.1, D2.2 (A), L3.1, P2.2 (Vin+)
unnamed: C19.1, P2.8 (CS)
unnamed: D2.1 (K), R4.2
unnamed: D19.2 (A), R99.1
unnamed: D20.1 (K), R100.1
unnamed: D21.2 (A), R101.1
unnamed: D22.2 (A), F1.1
unnamed: L1.2, R2.1
unnamed: L2.2, R3.1
unnamed: L4.2, R5.1
unnamed: L5.2, R6.1
unnamed: P1.3 (Vout+), R5.2
unnamed: P1.5 (Vout-), R6.2
unnamed: P2.3 (Ctrl), U1.1 (Out_NC)
unnamed: R4.1, U1.2 (COM_1)
PECL_high: R9.2, R10.1; also elsewhere on the board
PECL_low: R7.2, R8.1; also elsewhere on the board

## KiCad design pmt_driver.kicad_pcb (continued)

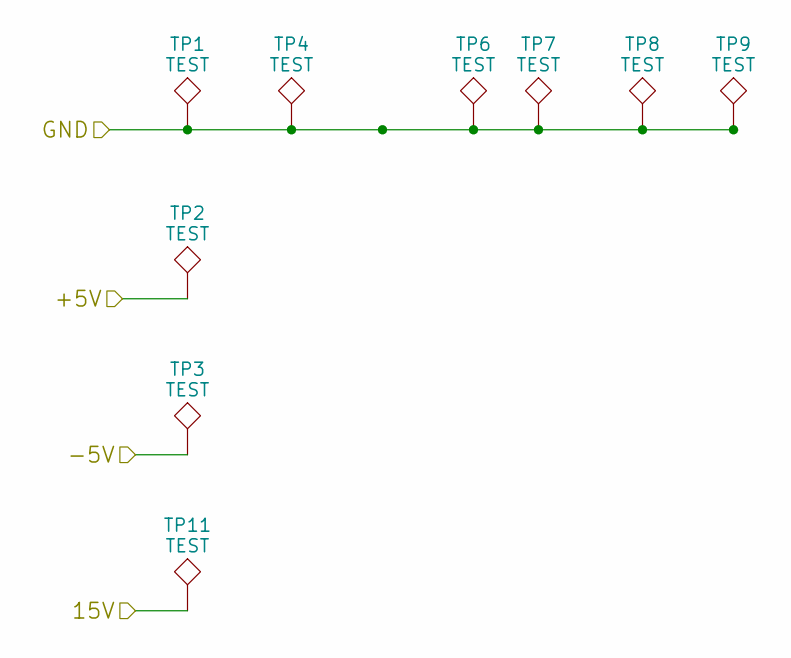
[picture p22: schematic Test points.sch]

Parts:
TP1, TP2, TP3, TP4, TP6, TP7, TP8, TP9, TP11: TEST; Test_Point_Keystone_5000-5004_Miniature

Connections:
+5V: TP2.1; also elsewhere on the board
+15V: TP11.1; also elsewhere on the board
-5V: TP3.1; also elsewhere on the board
GND: TP1.1, TP4.1, TP6.1, TP7.1, TP8.1, TP9.1; also elsewhere on the board

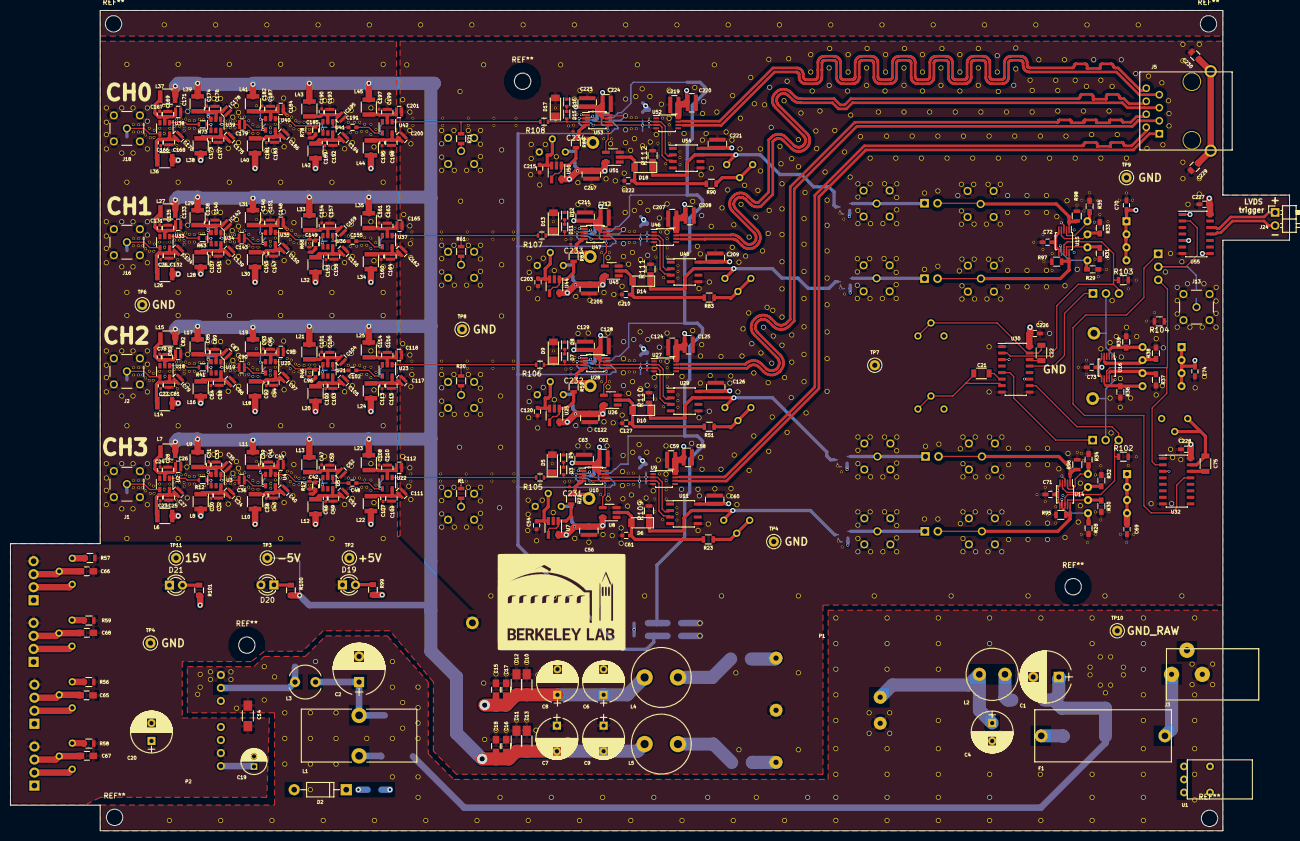
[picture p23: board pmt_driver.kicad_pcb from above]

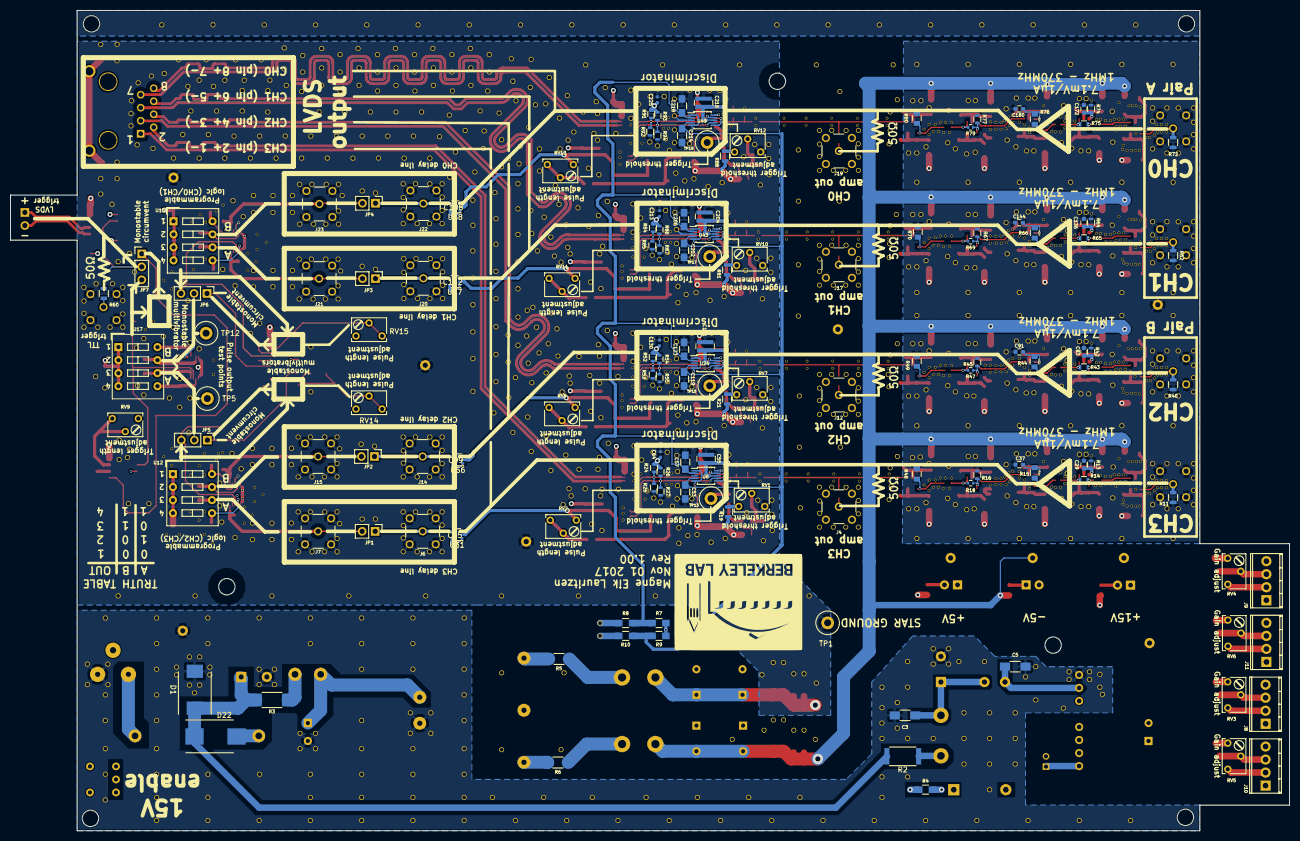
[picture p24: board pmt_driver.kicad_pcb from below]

Board: 4 copper layers, 249.5 x 160.0 mm, 537 parts (146 on the bottom side), 233 nets.

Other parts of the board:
C45, C99, C152, C188: 2.2u; C_0402_NoSilk
C65, C66, C67, C68: 1n; C_0805_HandSoldering
J6, J7, J14, J15, J20, J21, J22, J23: Conn_Coaxial; LEMO_straight
J8, J9, J10, J11: Screw_Terminal_01x04; TerminalBlock_Pheonix_MPT-2.54mm_4pol
JP1, JP2, JP3, JP4: Jumper; Pin_Header_Straight_1x02_Pitch2.54mm
R56, R57, R58, R59: 7.15k; R_0805
R95, R96, R97, R98: 50; R_0805
RV3, RV4, RV5, RV6: 10k; Potentiometer_Trimmer_Bourns_3266W
TP4#2: TEST; Test_Point_Keystone_5000-5004_Miniature

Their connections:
+5V: C45.1, C99.1, C152.1, C188.1; also elsewhere on the board
+15V: J8.1, J9.1, J10.1, J11.1; also elsewhere on the board
/Jumper 2/TTL_IN: J14.1, JP2.1; also elsewhere on the board
/Jumper 3/TTL_IN: J20.1, JP3.1; also elsewhere on the board
/Jumper 4/TTL_IN: J22.1, JP4.1; also elsewhere on the board
/Jumper/TTL_IN: J6.1, JP1.1; also elsewhere on the board
/Logic/PAIR_A_1: J7.1, JP1.2, R95.1; also elsewhere on the board
/Logic/PAIR_A_2: J15.1, JP2.2, R96.1; also elsewhere on the board
/Logic/PAIR_B_1: J21.1, JP3.2, R97.1; also elsewhere on the board
/Logic/PAIR_B_2: J23.1, JP4.2, R98.1; also elsewhere on the board
GND: C45.2, C65.2, C66.2, C67.2, C68.2, C99.2, C152.2, C188.2, J6.2, J7.2, J8.4, J9.4, J10.4, J11.4, J14.2, J15.2, J20.2, J21.2, J22.2, J23.2, R56.2, R57.2, R58.2, R59.2, R95.2, R96.2, R97.2, R98.2, TP4#2.1; also elsewhere on the board
unnamed: C65.1, J8.3, RV3.2
unnamed: C66.1, J9.3, RV4.2
unnamed: C67.1, J10.3, RV5.2
unnamed: C68.1, J11.3, RV6.2
unnamed: J8.2, RV3.3
unnamed: J9.2, RV4.3
unnamed: J10.2, RV5.3
unnamed: J11.2, RV6.3
unnamed: R56.1, RV3.1
unnamed: R57.1, RV4.1
unnamed: R58.1, RV5.1
unnamed: R59.1, RV6.1

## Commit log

2017-10-26 version 1
    [Amplifier.sch, Amplifier_2.sch, Coax out.sch, Digikey BOM calculator.ods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]
2017-11-13 Schematic fixes and creation of doumentation for mounting components.
    [2017-10-26T16-39-04.csv, Component mounting list.ods, PMT driver 2 units.csv, Pmt driver 5 units BOM.csv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]
2017-12-13 Several bug fixes and improvements.
    [Amplifier.sch, Component mounting list.ods, Discriminator.sch, Logic.sch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]
2017-12-13 Fixed amplifier gain and bandwidth info on silkscreen.
    [pmt_driver.kicad_pcb]
2018-03-09 fixed panel cutout and added custom components and footprints
    [pmt_driver.kicad_pcb]
